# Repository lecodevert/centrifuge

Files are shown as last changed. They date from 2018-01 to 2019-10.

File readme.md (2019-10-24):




# Physique sans Frontières Centrifuge

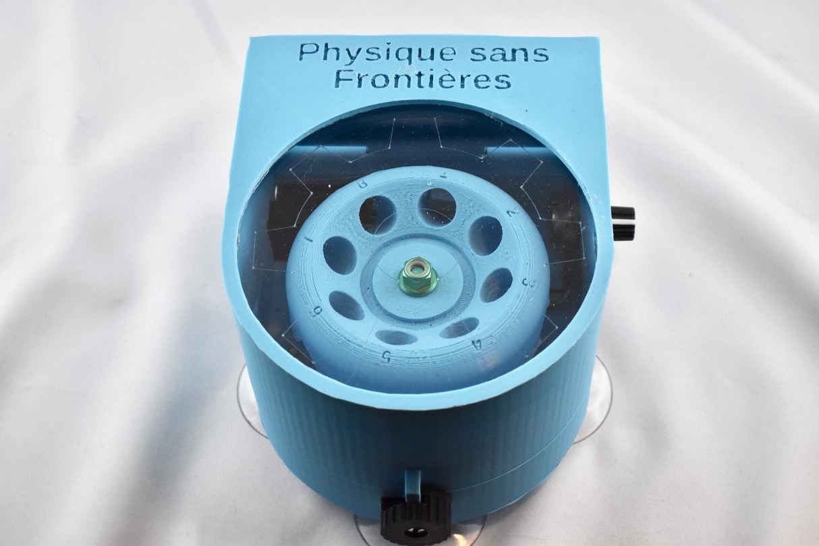
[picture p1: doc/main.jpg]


Designed for [PHYSIQUE SANS FRONTIÈRE](https://www.sfpnet.fr/commission/physique-sans-frontiere), a division of the [French Society of Physics](https://www.sfpnet.fr).

This 3D printed centrifuge uses a drone motor to spin 8 1.5ml Eppendorf tubes. It is also designed to be very cheap and accomodating of different parts for countries with limited access to such parts.

## Bill of Materials

| Name | Quantity | Price | Link |
|------|----------|-------|------|
| 12V power supply with barrel jack with 5x5/2.1mm barrel jack connector, power depends on the motor you use | 1 | depends | |
| female 5.5/2.1mm barrel jack connector with screw terminals | 1 | ? | |
| 12V SPST 10*15mm switch | 1 | ? | |
| B10k 10k Ohm Adjustment Single Linear Rotary Potentiometer | 1 | ? | |
| Digispark ATTINY85 | 1 | ? | |
| MT1806 2400KV CW/CCW Motor 1806 Mini Brushless Motor | 1 | ? | |
| BLHeli OPTO mini-16A ESC | 1 | ? | |
| 4mm screw | 1 | ? | |
| 4mm Suction cups | 4 | ? | |
| 3mm rod | 1 | ? | |
| acrylic window (optional) | 0-1 | ? | |

## Schematic

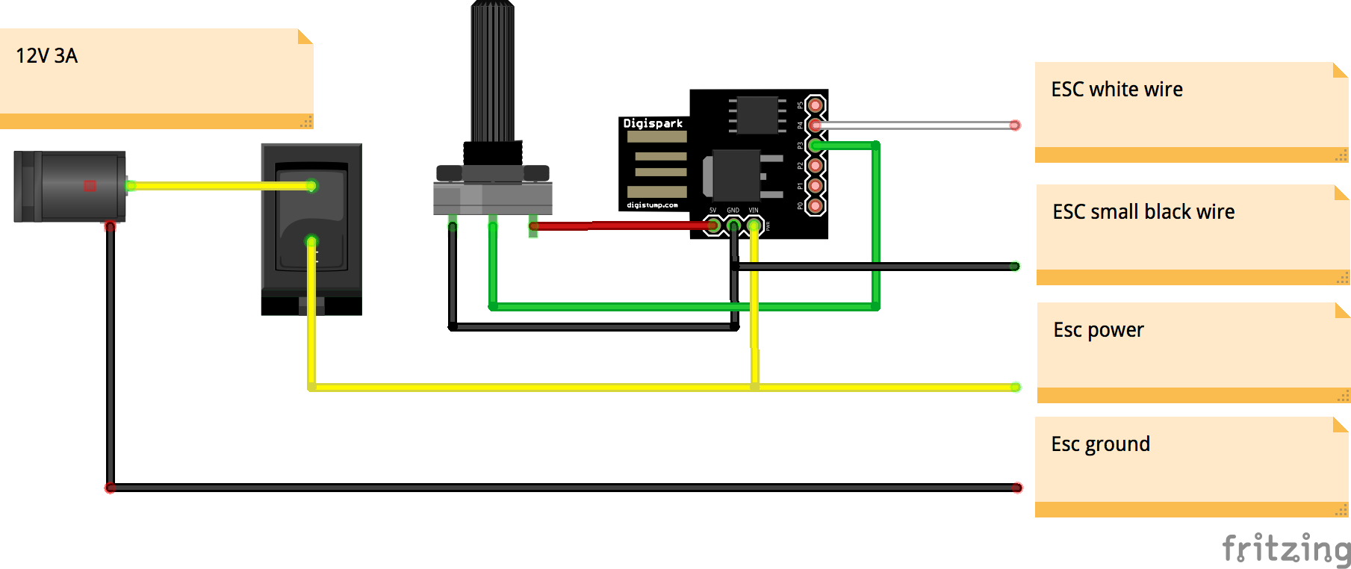
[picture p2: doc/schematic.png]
Schematic


## Instruction

### Hardware

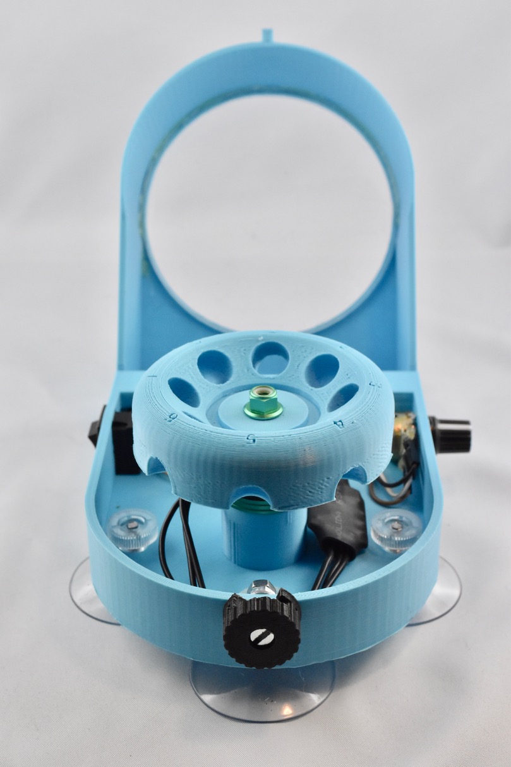
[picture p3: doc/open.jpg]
Opened


#### Printing

There is a couple of choices before hand:

If you want to have a window on the lid, you need to print [lid_window.stl](stl/lid_window.stl) and also use a laser cutter to cut and engrave [window.dxf](dxf/window.dxf) using acrylic.

Otherwise, just print [lid_no_window.stl](lid_no_window.stl).

For the motor, depending on the type you chose, print either [base_universal.stl](stl/base_universal.stl) for the beefier motors or [base_small_motor.stl](stl/base_small_motor.stl) for smaller motors that uses m3 holes spaced 16mm and 19mm.

Then print the rotor and the latch.

No parts needs supports except for the latch.

#### Preparing

The base needs some preparation: there is a couple of walls that needs to be removed on the inside where the power jack is situated. If there is some plastic that needs cleaning on the ceiling on the inside, remove it.

#### Software 

First, install [PlatformIO](http://platformio.org) on your platform of choice.

Run in the root directory of this project:

    pio run -t upload

And plug in the Digispark when it tells you to. Upload takes a couple of seconds.

Make sure no components are connected while uploading to the Digispark. Do the upload before soldering.

#### Soldering

You can solder the wires according for the schematics, except for the following:

 * The wires going to the switch, as it needs to be installed on the base first.
 * The wires connecting the ESC and the motor.

Drones motors comes in either CW (Clockwise) or CCW (Counter-clockwise) and needs to spin in their intended rotation direction otherwise the nut will unscrew itself and the rotor will fly in the direction of the nearest face.

To prevent that, do a test run using temporary connectors and invert the cables if the direction is not right. Only then solder them.

**Note** if the ESC has a wire for 5V, do not use it, only connect the Ground and Signal wires.

#### Assembly

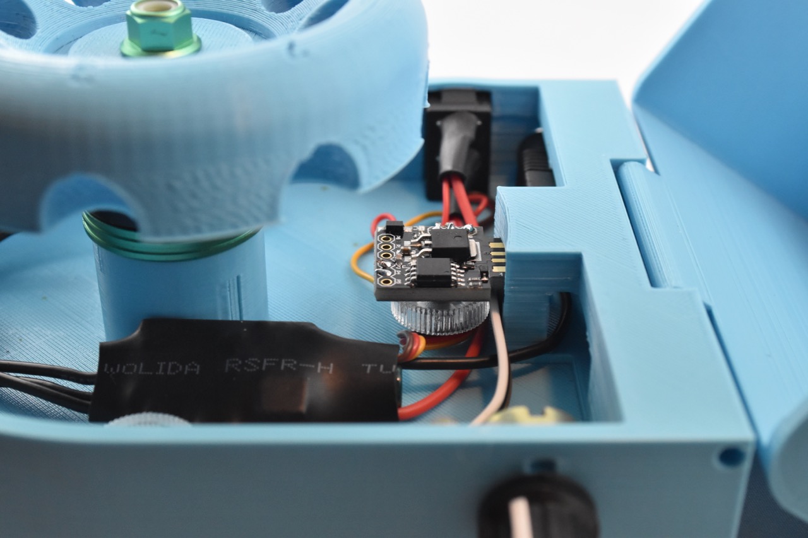
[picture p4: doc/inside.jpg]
inside


Start by a test fit of the barrel jack connector, it's a very tight fit on purpose and depending on the amount of rubber molding surrounding it, you might need to remove some of it.

 * Install the motor. It needs to be really secure. If using a big motor, use a metal bracket between the base and the motor.
 * Connect the barrel jack wires. One of them will do behind the center pilar.
 * Install the switch and connect/solder the wires to it.
 * Install the rotary potentiometer and secure it with the included nut and washer. Put on the included knob if any, or print one.
 * Install the 4 suction cups with their nuts.
 * Slide the digispark in the slot in the center pillar.
 * Screw in the latch using a 4mm bolt and a self locking nut on the front of the base.
 * Slide the rotor on the motor shaft and secure it using the nut included with the motor.
 * Glue in the window on inside of the lid using hot glue if applicable.
 * Assemble the base and the lid using a 3mm rod.

## Usage

 * Install the Eppendorf tubes in a balanced manner on the rotor.
 * Close the lid using the latch.
 * Plug in the power.
 * Switch on the centrifuge.
 * A short calibration procedure will start, lasting 10 seconds.
 * You can now select the speed using the knob.

## Attribution

The rotor comes from Biohack Academy's OpenFuge

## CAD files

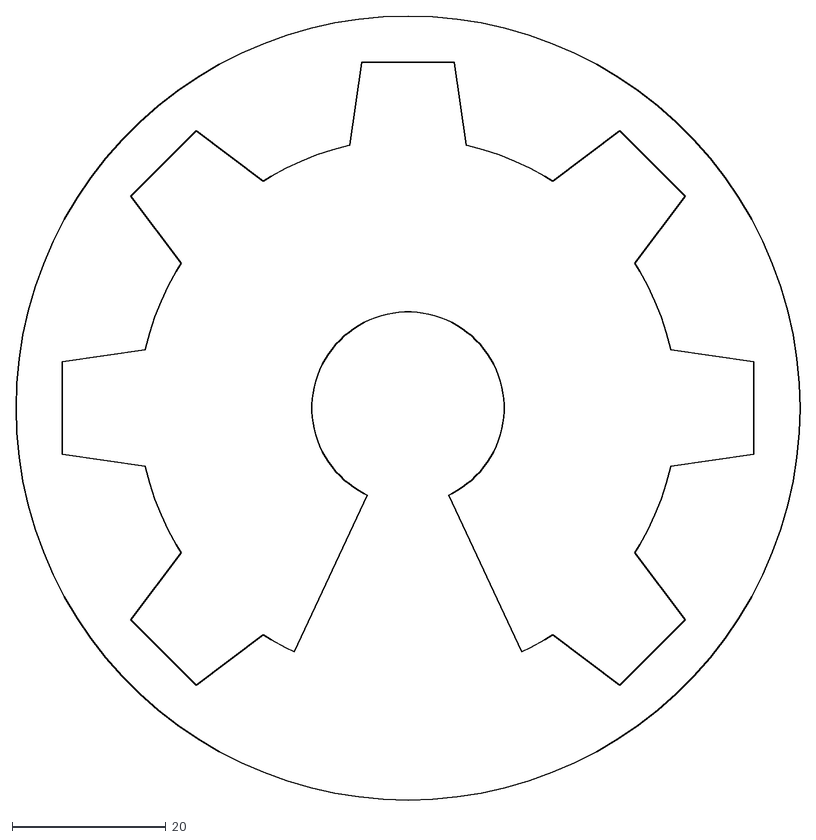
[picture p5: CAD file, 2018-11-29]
dxf/window.dxf
102.0 x 102.0

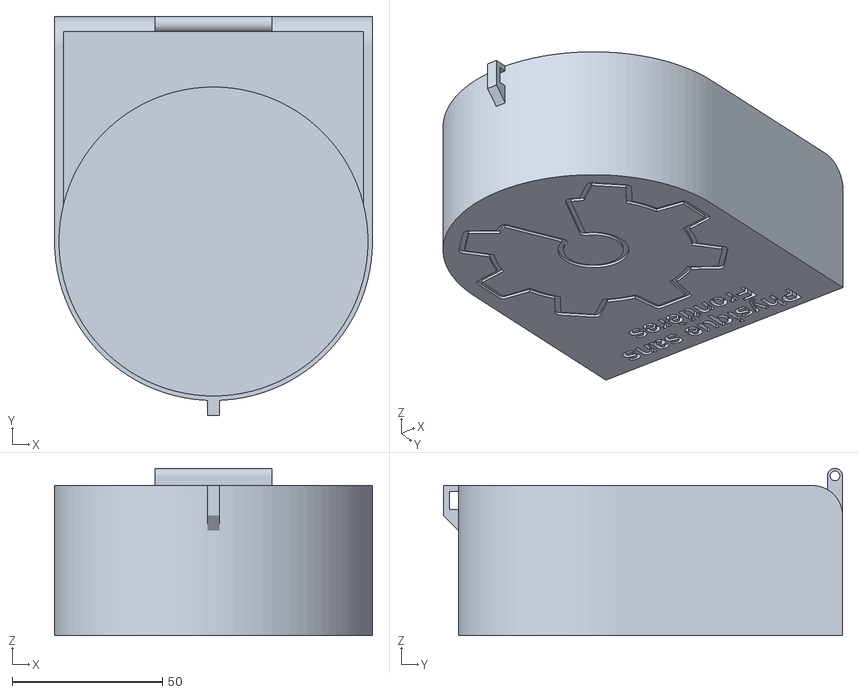
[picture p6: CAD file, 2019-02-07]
stl/lid_no_window.stl
106.0 x 133.0 x 55.8

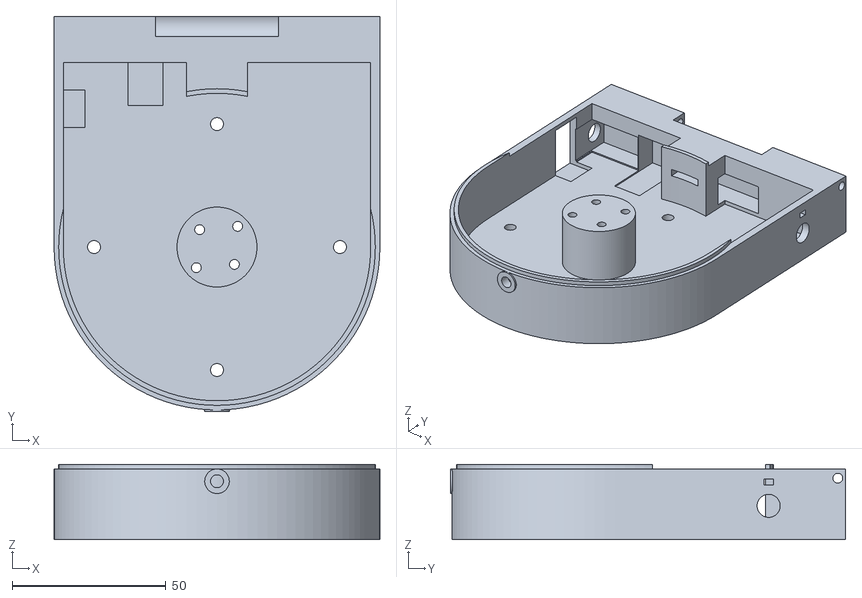
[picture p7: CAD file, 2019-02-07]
stl/base_small_motor.stl
106.0 x 128.5 x 24.5

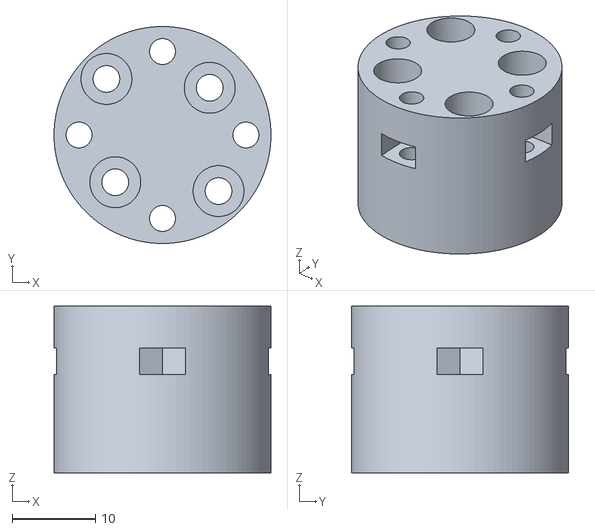
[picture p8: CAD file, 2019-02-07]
stl/motor_spacer.stl
26.0 x 26.0 x 20.0

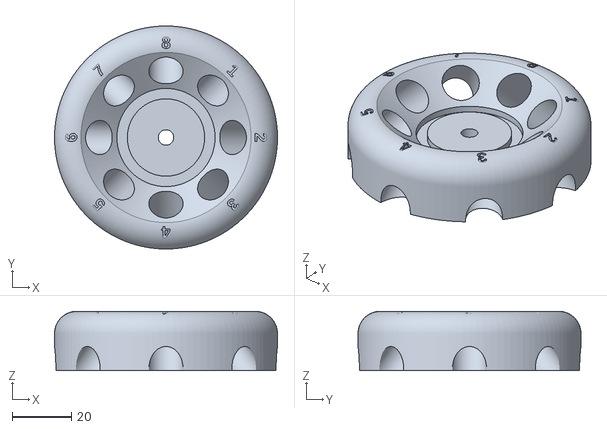
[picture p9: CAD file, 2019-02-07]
stl/rotor.stl
75.0 x 75.0 x 20.0

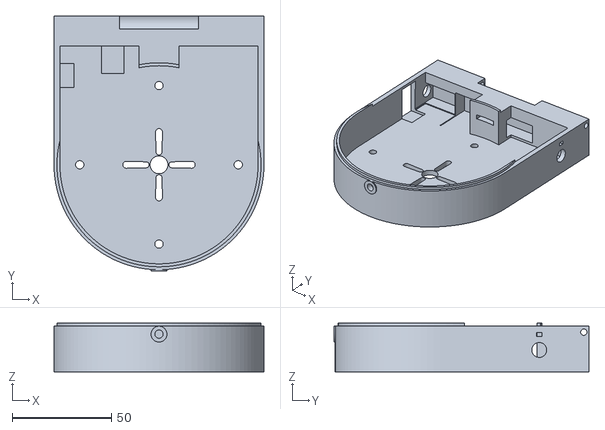
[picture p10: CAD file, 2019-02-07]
stl/base_universal.stl
106.0 x 128.5 x 24.5

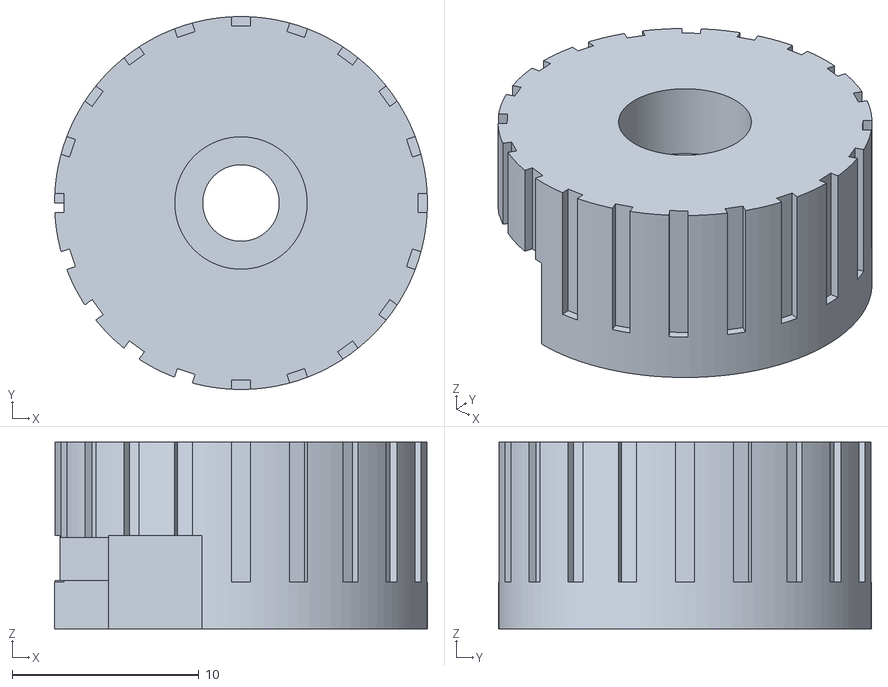
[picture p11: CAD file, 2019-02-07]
stl/latch.stl
20.0 x 20.0 x 10.0

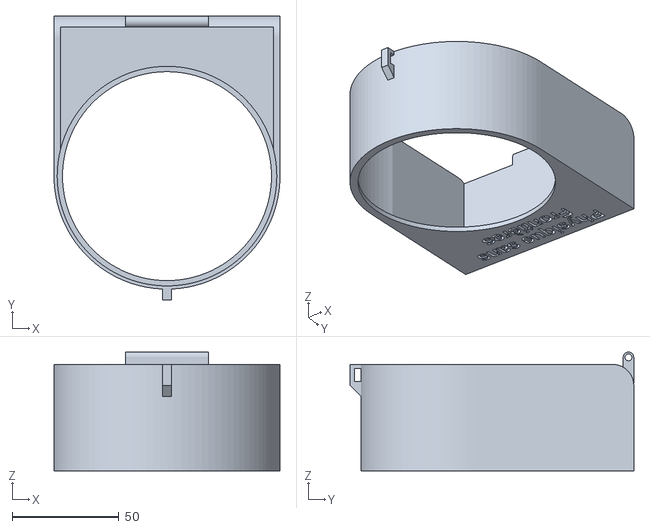
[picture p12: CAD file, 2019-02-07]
stl/lid_window.stl
106.0 x 133.0 x 55.8

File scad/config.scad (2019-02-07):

// Global Parameters
$fn = 100;
clearance = 0.1;

// Base
inner_dia = 100; // Inside diameter of the main chamber
base_hei = 20;
base_thi = 3;
base_dia = inner_dia + 2 * base_thi;
total_base_hei = base_hei + base_thi;
lip_size = 1.5;

hinge_rad = 10;
hinge_depth = 75;
hinge_thi = 5;

// Latch
knob_hei = 10;
knob_dia = 20;
latch_hook_thi = 2;
latch_hole_hei = 19;

// Lid
lid_wall_thi = 3;
lid_dia = inner_dia + 2 * lid_wall_thi;
lid_height = 50;

// Rotor
rotor_shaft_dia = 5;
axis_radius = rotor_shaft_dia/2 + clearance; // radius of the motor shaft

tube_radius = 5.75; // inner radius of the tube holders
tube_angle = 45; // angle in the rotor
tube_pos = 47.5; // position of tube holders

text1 = "Physique sans";
text2 = "Frontières";
font = "Liberation Sans:style=Bold";

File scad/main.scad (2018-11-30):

include <motor_spacer.scad>;
include <base.scad>;
include <config.scad>;
include <latch.scad>;
include <lid.scad>;
include <rotor.scad>;
include <window.scad>;

draw_complete = 1;
draw_base_universal = 0;
draw_base_small_motor = 0;
draw_lid_window = 0;
draw_lid_no_window = 0;
draw_latch = 0;
draw_rotor = 0;
draw_motor_spacer = 0;
draw_window = 0;

if (draw_complete == 1) {
    color("white") base();
    color("green") translate([0, 0, 40]) rotor();
    color("gray") translate([0, 0, base_hei + base_thi]) lid();
    color("red") translate([0, -base_dia/2 + base_thi /2 -2, latch_hole_hei])
        rotate([90, 90, 0]) latch();
}
else if (draw_base_small_motor == 1) base(mount="small");
else if (draw_base_universal == 1) base(mount="universal");
else if (draw_latch == 1) latch();
else if (draw_lid_window == 1) rotate([0, 180, 0]) lid();
else if (draw_lid_no_window == 1) rotate([0, 180, 0]) lid(false);
else if (draw_motor_spacer == 1) rotate([0, 180, 0]) motor_spacer();
else if (draw_rotor == 1) rotor();
else if (draw_window == 1) window();

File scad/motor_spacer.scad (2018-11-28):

module nut_trap(w = 5.5, h = 3) {
    cylinder(r = w/2/cos(180/6) + 0.05, h=h, $fn=6);
    translate([0, - w/2, 0]) cube([10, w, h]);
}

// Made to mount motors with m3 holes spaced 16mm and 19mm in each direction
module motor_spacer(h = 20, mount = "universal") {
    difference() {
        cylinder(d=26, h=h);
        for(i=[45: 180: 270])
            rotate([0, 0, i]) {
                translate([19/2, 0, h - 5.5])
                    cylinder(d=3 + clearance*2, h=6);
                translate([19/2, 0, -1])
                    cylinder(d=6 + clearance, h=h-4);
            }
        for(i=[135: 180: 360])
            rotate([0, 0, i]) {
                translate([16/2, 0, h - 5.5])
                    cylinder(d=3 + clearance*2, h=6);
                translate([16/2, 0, -1])
                    cylinder(d=6 + clearance, h=h-4);
            }
        if (mount == "universal") {
            for(i=[0: 90: 270])
                rotate([0, 0, i]) {
                    translate([10, 0, -0.5])
                        cylinder(d=3 + clearance, h=h+1);
                    translate([10, 0, 5])
                        nut_trap(w = 5.5, h = 3 + clearance*2);
                }
        }
    }
}

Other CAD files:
scad/base.scad
scad/latch.scad
scad/lid.scad
scad/oshw_logo.scad
scad/rotor.scad
scad/window.scad

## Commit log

2018-01-25 Initial Import
    [V2_Body_fixed.stl, V2_Cover_fixed.stl, V2_Feet.stl, V2_MotorMount.stl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]
2018-07-26 Added scad files
    [main.scad, rotor.scad]
2018-07-26 preliminary latch
    [main.scad]
2018-07-30 latch holes
    [main.scad]
2018-07-30 added void inside lid to reduce amount of plastic used
    [main.scad]
2018-07-30 added latch
    [main.scad]
2018-09-12 Added makefile and regenerated output files
    [V2_Body_fixed.stl, V2_Cover_fixed.stl, V2_Feet.stl, V2_MotorMount.stl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]
2018-11-22 added text to lid
    [main.scad]
2018-11-26 integrating rotor source more closely
    [main.scad, rotor.scad]
2018-11-26 converted rotor source to mm instead of cm
    [main.scad, rotor.scad]
2018-11-26 added numbering labels to the rotor's tubes
    [main.scad, rotor.scad]
2018-11-26 countersunk hole for latch bolt
    [main.scad]
2018-11-26 Split scad files
    [base.scad, config.scad, lid.scad, main.scad]
2018-11-28 Added motor spacer
    [motor_spacer.scad]
2018-11-28 Tweaks before release
    [base.scad, config.scad, latch.scad, lid.scad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]
2018-11-28 OSHW logo
    [lid.scad, oshw_logo.scad]
2018-11-29 added window DXF file for laser cutting
    [main.scad, window.dxf, window.scad]
2018-11-30 Working automatic ESC calibration
2018-11-30 text tweaks
    [config.scad, lid.scad, main.scad, rotor.scad]
2018-11-30 Exported STL files
    [base.stl, base_small_motor.stl, base_universal.stl, latch.stl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]
2019-01-21 Documentation update
    [latch.scad, latch.stl, main.scad]
2019-01-21 Activation travis ci
    [base_small_motor.stl, base_universal.stl, latch.stl, lid_no_window.stl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]
2019-02-07 Added lip to base to prevent lid slipping
    [base.scad, base_small_motor.stl, base_universal.stl, config.scad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]
